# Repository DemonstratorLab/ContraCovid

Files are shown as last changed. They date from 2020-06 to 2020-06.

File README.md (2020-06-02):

[][cc-by-nc-sa]

# ContraCovid
Demonstrator Lab against SARS-CoV2

# Work in Progress
This repository is a work in progress. It currently contains the minimum of files needed to get started producing face shields. More and better information, tools and other content will be added in the comming days. (02-06-2020)

# Structure
This repository currently contains only one project: Face-Shield. Please view the Face-Shield directory for more information. 

# License
This work is licensed under [CC BY-NC-SA 4.0][cc-by-nc-sa]  
[][cc-by-nc-sa]

[cc-by-nc-sa]: http://creativecommons.org/licenses/by-nc-sa/4.0/
[cc-by-nc-sa-image]: https://licensebuttons.net/l/by-nc-sa/4.0/88x31.png
[cc-by-nc-sa-shield]: https://img.shields.io/badge/License-CC%20BY--NC--SA%204.0-lightgrey.svg

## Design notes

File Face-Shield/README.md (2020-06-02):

# Instructions
A PDF with instructions is provided. 

# Structure
This project is split into several directories. 

### Parts
The parts directory contains all parts you need to produce the actual face shield. Each part has it's own subdirectory. 
Each part directory contains the DXF files and instructions to produce a part. This should be enough to create it. However, we also provide the original designs from which the DXF files were created. 

# Tools
The designs for tools we used are also provided. Note: These tools were designed specifically for our machine and use-case. Though we think the ideas and some of the desings may be usefull, some modifications will likely be needed.

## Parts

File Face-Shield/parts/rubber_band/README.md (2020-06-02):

Rubber band

# Rubber band
The rubber band keeps the shield in place. It is in contact with skin and hair and as such, should be safe and comfortable to wear. 

# Design decissions
- Silicone rubber was chosen because it is highly inert and generally considerd not to irritate the skin nor create allergic reactions. 
- 1mm thick material was easily obtainable for us and proved to be strong enough. We have not experimented with other thicknesses. 
- The corners of the holes were slightly rounded. This almost doubled the strength of the band. 

# Laser cut pattern
The pattern is provided as a DXF file generated from the design file(s). The DXF file is already compensated for a kerf of 0.15mm. This is the typical kerf for a correctly set up CO2 laser in silicone rubber. Small differences in kerf width will not change the functionality. However, the user is adviced to check this. 

# Design files
This part was designed in Fusion 360. The latest 'production-ready' source is provided as Fusion 360 f3d file and STEP file. 

# Set-up sheet / Lightburn file
The provided Lightburn file contains the program we use to cut 25 bands from a 505mm x 305mm sheet of Silicone Rubber. It can be used as a basis for your setup, but will likely need to be changed

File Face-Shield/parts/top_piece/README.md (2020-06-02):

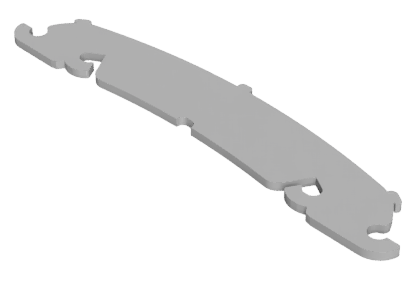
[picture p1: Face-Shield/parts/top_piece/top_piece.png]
top piece


# Laser cut pattern
The pattern is provided as a DXF file generated from the design file(s). The DXF file is already compensated for a kerf of 0.45mm, which is assumed to be typical for cutting HDPE. However, the user is adviced to verify this assumption. 

# Design files
This part was designed in Fusion 360. The latest 'production-ready' source is provided as Fusion 360 f3d file and STEP file.

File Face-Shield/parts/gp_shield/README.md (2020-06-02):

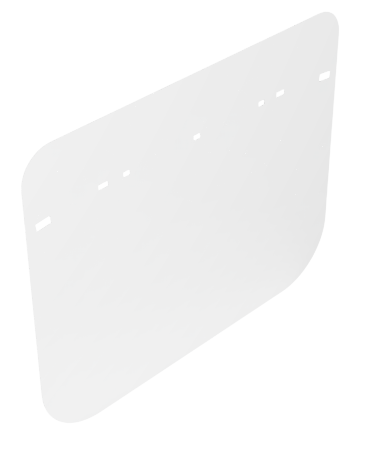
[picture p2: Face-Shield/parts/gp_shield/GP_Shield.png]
General Practicioner shield


# Laser cut pattern
The pattern is provided as a DXF file generated from the design file(s). The DXF file is already compensated for a kerf of 0.15mm, which is assumed to be typical for cutting (A)PET. However, the user is adviced to verify this assumption. 

# Design files
This part was designed in Fusion 360. The latest 'production-ready' source is provided as Fusion 360 f3d file and STEP file.

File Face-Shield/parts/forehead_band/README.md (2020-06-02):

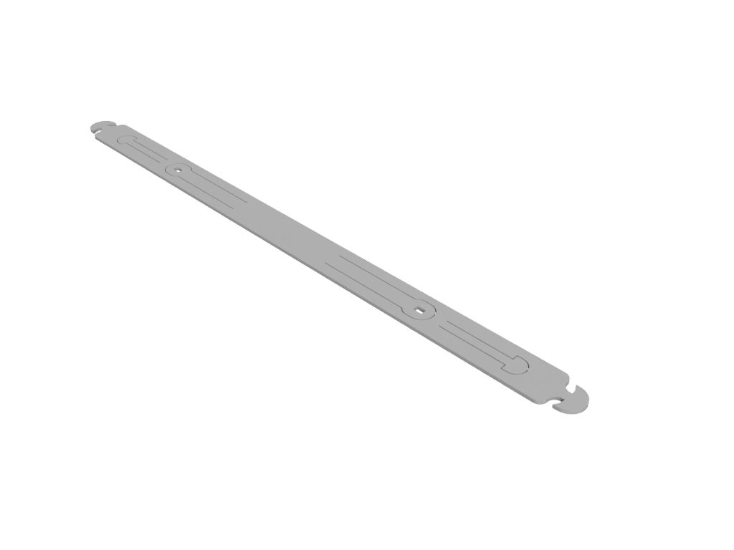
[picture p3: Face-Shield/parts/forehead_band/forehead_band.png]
Forehead band


# Laser cut pattern
The pattern is provided as a DXF file generated from the design file(s). The DXF file is already compensated for a kerf of 0.45mm, which is assumed to be typical for cutting HDPE. However, the user is adviced to verify this assumption. 

# Design files
This part was designed in Fusion 360. The latest 'production-ready' source is provided as Fusion 360 f3d file.  
A STEP file is also included. However, the STEP format does not support sketches. Therefore, an additional DXF file (internal_cuts.dxf) is provided for the internal cuts.  
Other formats are available upon request.

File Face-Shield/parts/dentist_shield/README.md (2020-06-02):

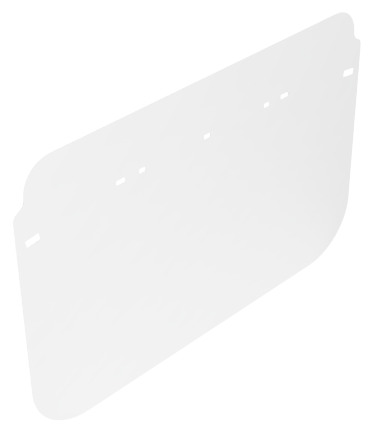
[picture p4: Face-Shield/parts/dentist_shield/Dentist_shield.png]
Part image


# Laser cut pattern
The pattern is provided as a DXF file generated from the design file(s). The DXF file is already compensated for a kerf of 0.15mm, which is assumed to be typical for cutting (A)PET. However, the user is adviced to verify this assumption. 

# Design files
This part was designed in Fusion 360. The latest 'production-ready' source is provided as Fusion 360 f3d file and STEP file.

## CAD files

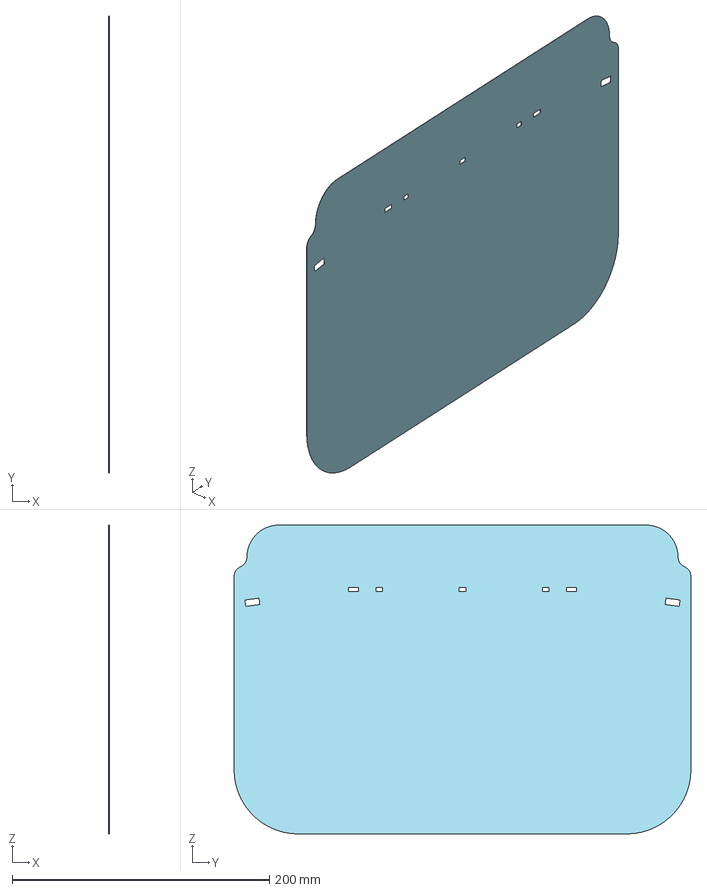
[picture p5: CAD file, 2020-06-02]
Face-Shield/parts/dentist_shield/Dentist_shield.step
0.2 x 355.0 x 240.0 mm

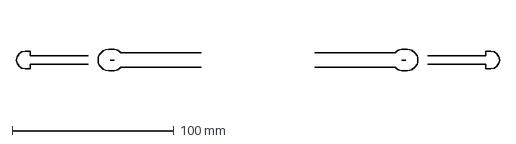
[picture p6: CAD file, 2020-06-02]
Face-Shield/parts/forehead_band/inside_cuts.dxf
299.0 x 13.0 mm

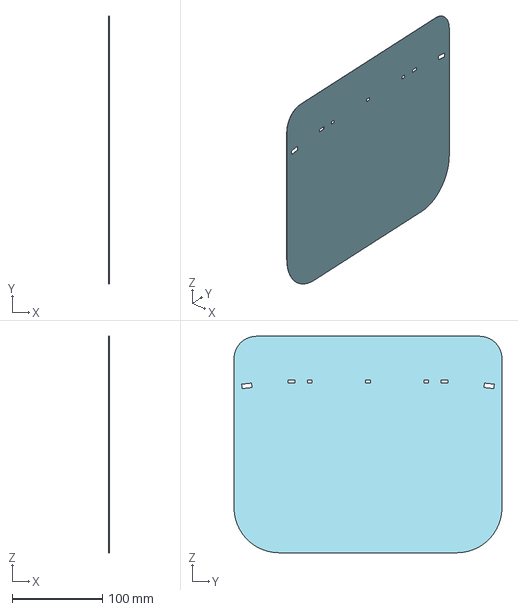
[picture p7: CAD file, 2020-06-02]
Face-Shield/parts/gp_shield/GP_Shield.step
0.2 x 297.0 x 240.0 mm

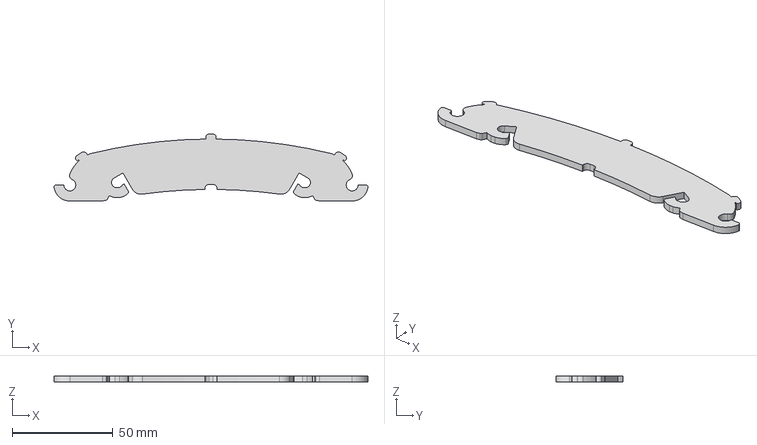
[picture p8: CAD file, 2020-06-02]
Face-Shield/parts/top_piece/top_piece.step
155.7 x 33.2 x 3.00 mm

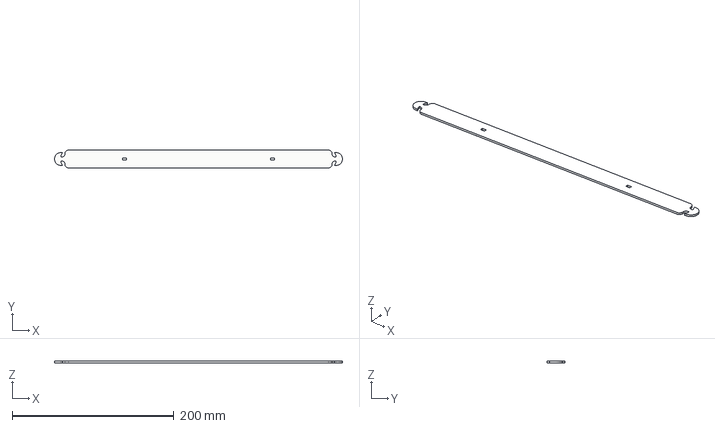
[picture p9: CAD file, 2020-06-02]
Face-Shield/parts/forehead_band/forehead_band.step
356.0 x 22.0 x 2.00 mm

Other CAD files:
Face-Shield/parts/dentist_shield/Dentist_shield.dxf
Face-Shield/parts/dentist_shield/Dentist_shield.f3z
Face-Shield/parts/forehead_band/forehead_band.dxf
Face-Shield/parts/forehead_band/forehead_band.f3d
Face-Shield/parts/gp_shield/GP_Shield.dxf
Face-Shield/parts/gp_shield/GP_Shield.f3z
Face-Shield/parts/top_piece/top_piece.dxf
Face-Shield/parts/top_piece/top_piece.f3d

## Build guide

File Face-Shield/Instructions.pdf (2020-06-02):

# Face Shield Building Instructions

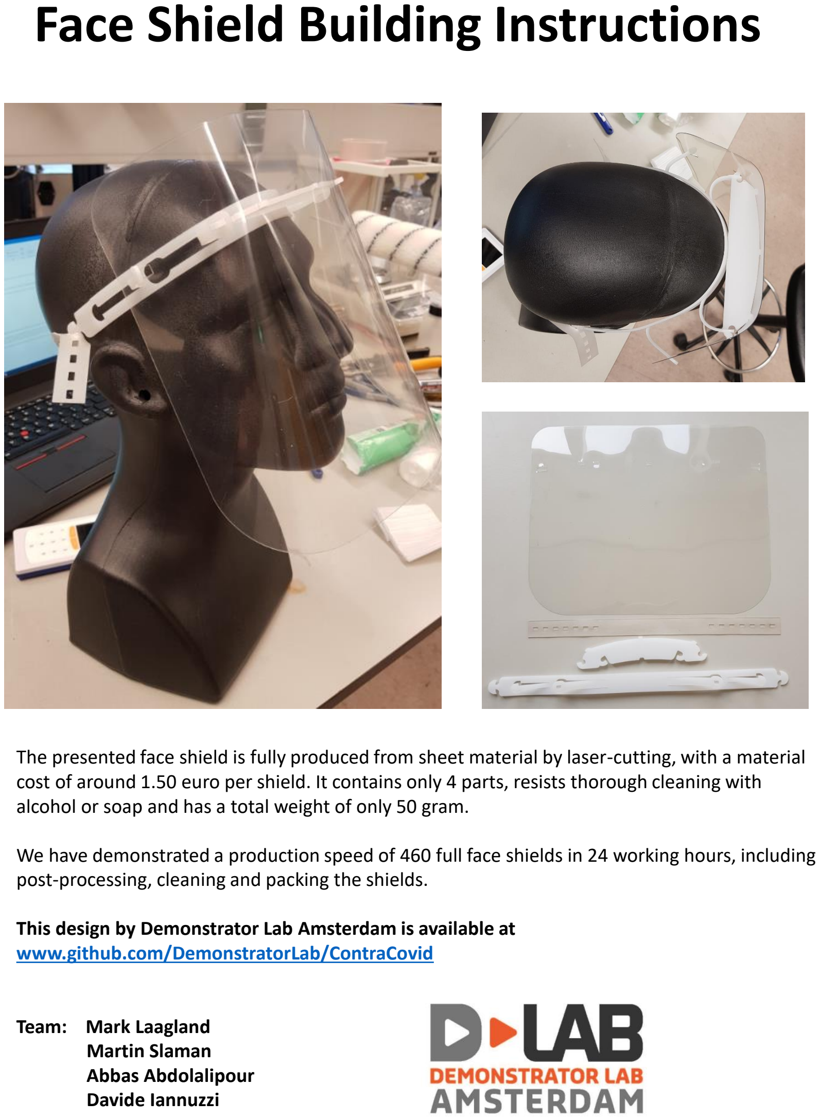
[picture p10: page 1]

The presented face shield is fully produced from sheet material by laser-cutting, with a material cost of around 1.50 euro per shield. It contains only 4 parts, resists thorough cleaning with alcohol or soap and has a total weight of only 50 gram.

We have demonstrated a production speed of 460 full face shields in 24 working hours, including post-processing, cleaning and packing the shields.

This design by Demonstrator Lab Amsterdam is available at www.github.com/DemonstratorLab/ContraCovid

Team: Mark Laagland
Martin Slaman
Abbas Abdolalipour
Davide Iannuzzi

# The shield part:

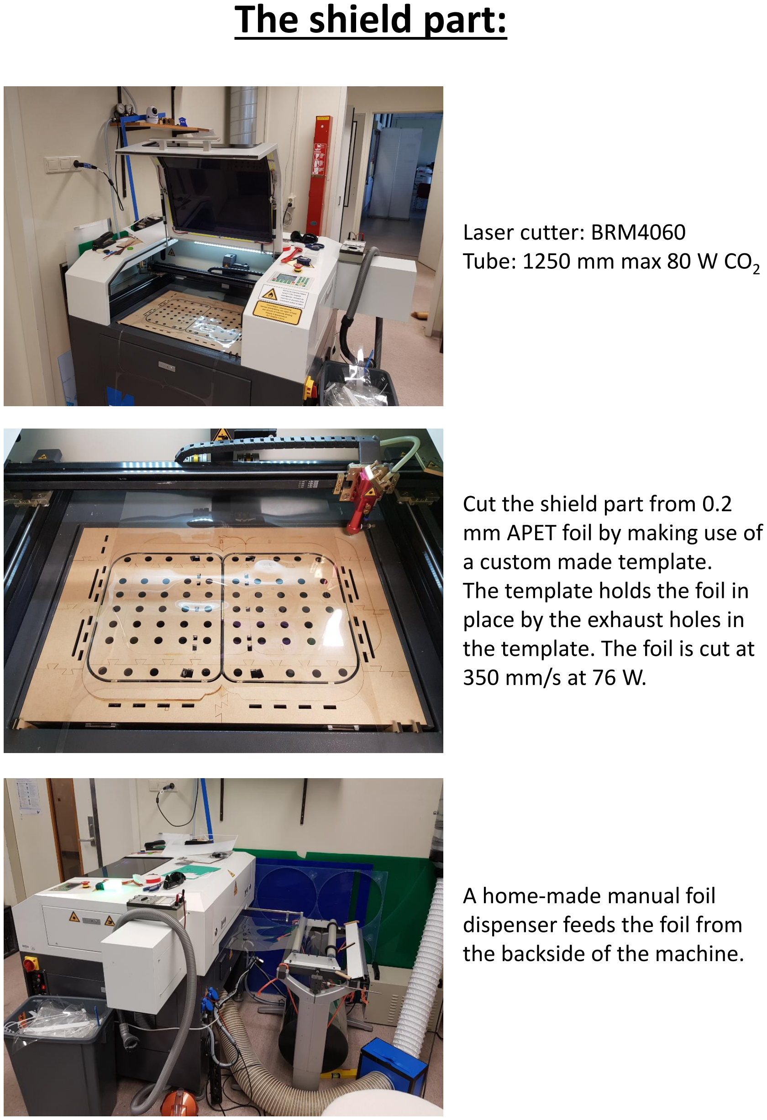
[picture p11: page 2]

Laser cutter: BRM4060
Tube: 1250 mm max 80 W CO2

Cut the shield part from 0.2 mm APET foil by making use of a custom made template.
The template holds the foil in place by the exhaust holes in the template. The foil is cut at 350 mm/s at 76 W.

A home-made manual foil
dispenser feeds the foil from the backside of the machine.

# The frame parts:

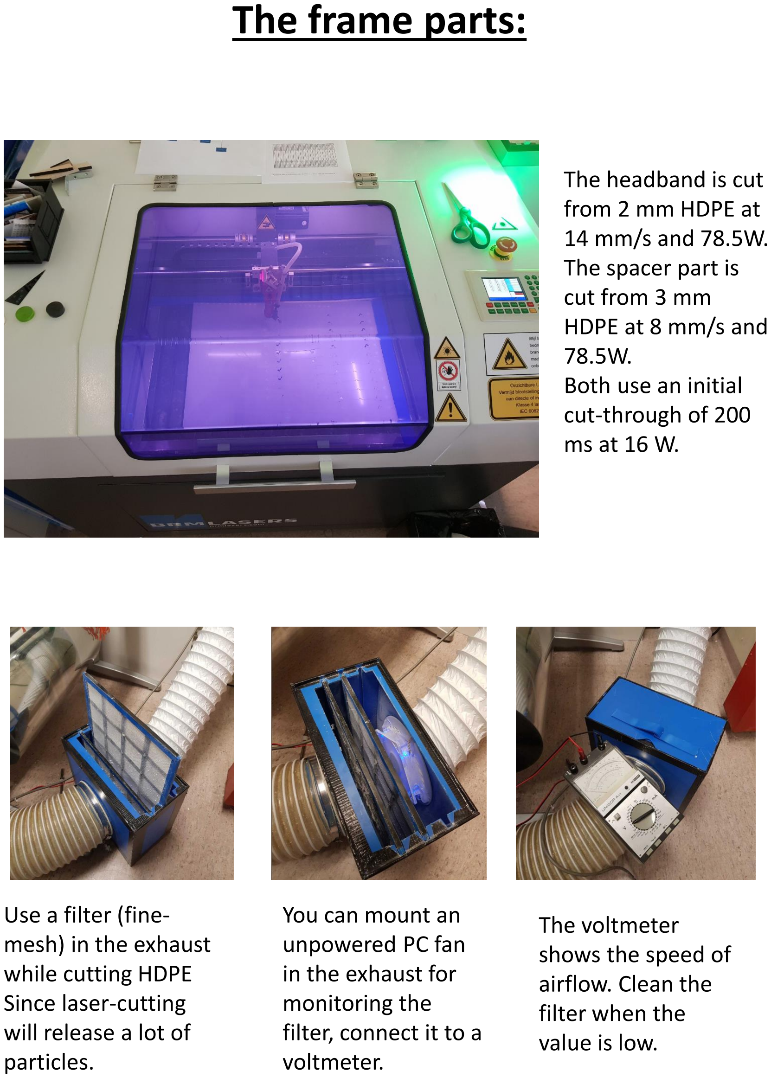
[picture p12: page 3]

Use a filter (fine-mesh) in the exhaust
while cutting HDPE
Since laser-cutting
will release a lot of
particles.

You can mount an
unpowered PC fan
in the exhaust for
monitoring the
filter, connect it to a
voltmeter.

The voltmeter
shows the speed of
airflow. Clean the
filter when the
value is low.

The headband is cut
from 2 mm HDPE at
14 mm/s and 78.5W.
The spacer part is
cut from 3 mm
HDPE at 8 mm/s and
78.5W.
Both use an initial
cut-through of 200
ms at 16 W.

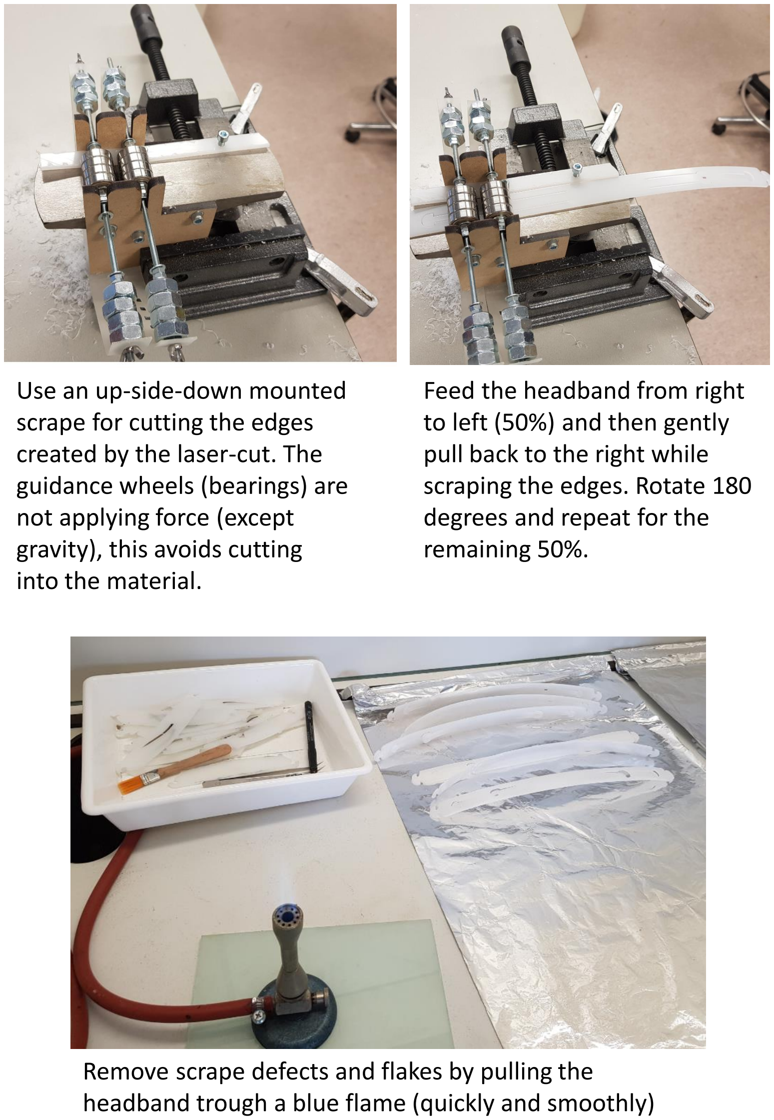
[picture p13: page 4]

Use an up-side-down mounted scrape for cutting the edges created by the laser-cut. The guidance wheels (bearings) are not applying force (except gravity), this avoids cutting into the material.

Feed the headband from right to left (50%) and then gently pull back to the right while scraping the edges. Rotate 180 degrees and repeat for the remaining 50%.

Remove scrape defects and flakes by pulling the headband trough a blue flame (quickly and smoothly)

# The elastic band:

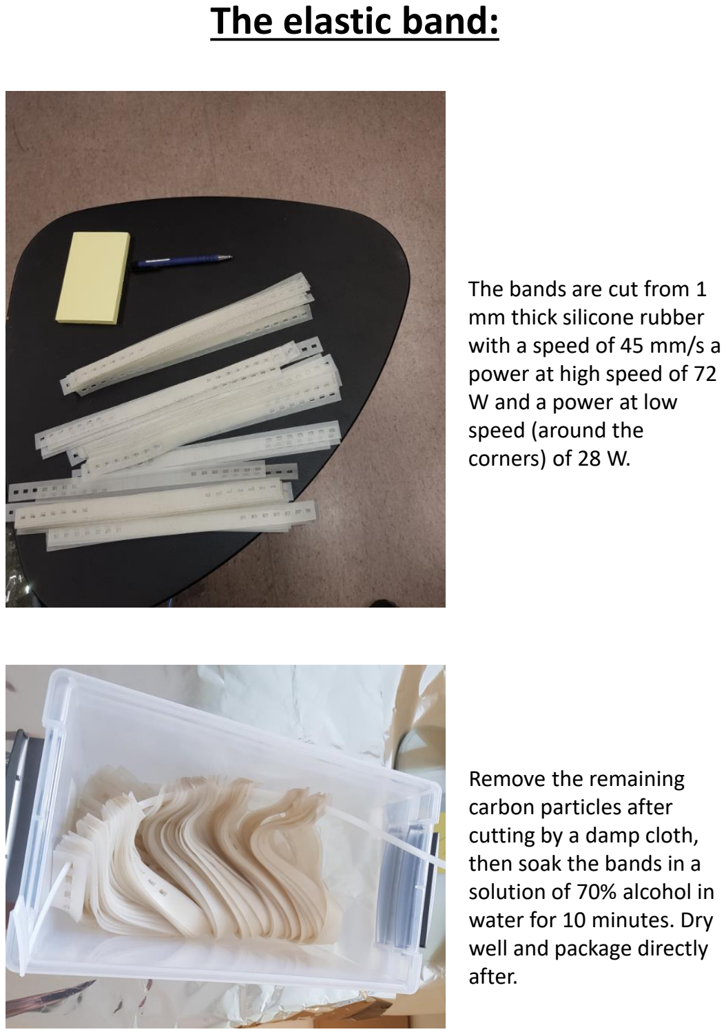
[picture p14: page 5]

The bands are cut from 1
mm thick silicone rubber
with a speed of 45 mm/s a
power at high speed of 72
W and a power at low
speed (around the
corners) of 28 W.

Remove the remaining
carbon particles after
cutting by a damp cloth,
then soak the bands in a
solution of 70% alcohol in water for 10 minutes. Dry
well and package directly
after.

# Face shield assembly:

1) Clean hands thoroughly for 20 seconds with soap and water
2) Fold the headband as pictured, keep the smooth side inwards to the forehead
3) Connect the spacer part (two hooks) to the headband (two holes)
4) Connect the rubber band
5) Connect the shield to the spacer, bend the arrowheads of the headband to connect them to the shield.

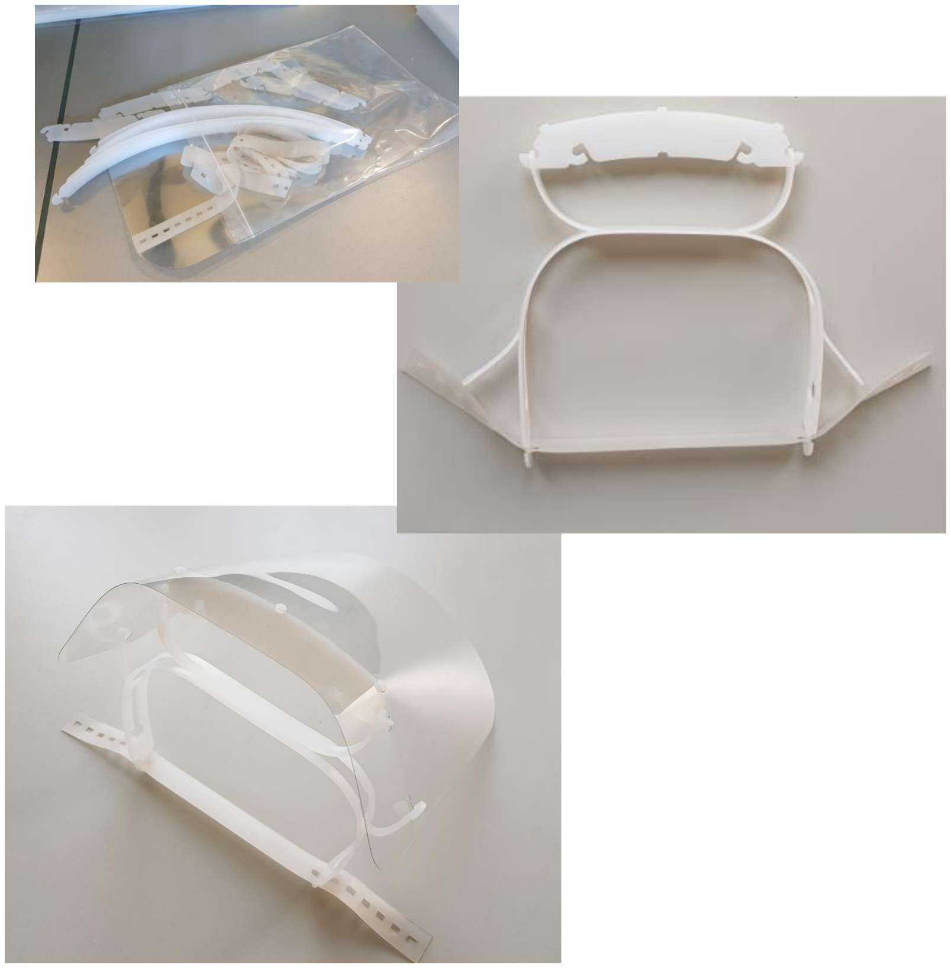
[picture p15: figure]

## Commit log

2020-06-02 Initial information
    [Dentist shield.dxf, Dentist shield.f3z, Dentist shield.step, GP Shield v7.step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]
2020-06-02 Renamed files for easier referencing
    [Dentist_shield.dxf, Dentist_shield.f3z, Dentist_shield.step, GP_Shield.dxf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]
